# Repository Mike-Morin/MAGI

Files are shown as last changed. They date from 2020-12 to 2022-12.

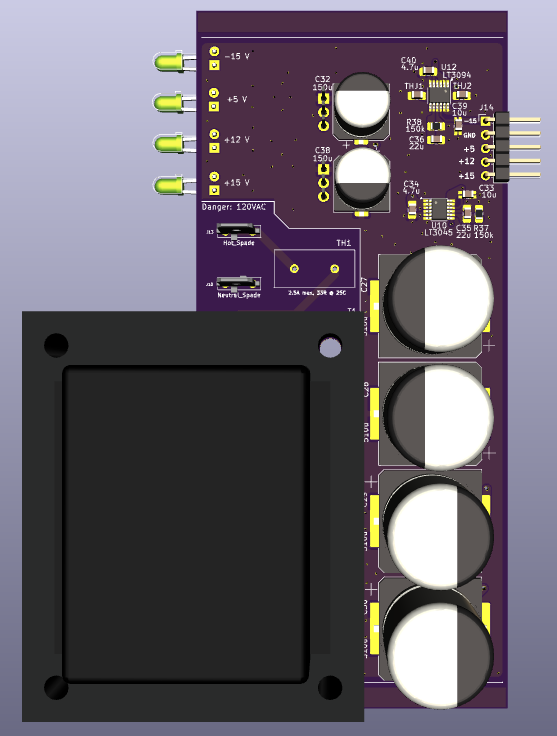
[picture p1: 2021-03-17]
SMU Test Fixture/Images/top3d.png

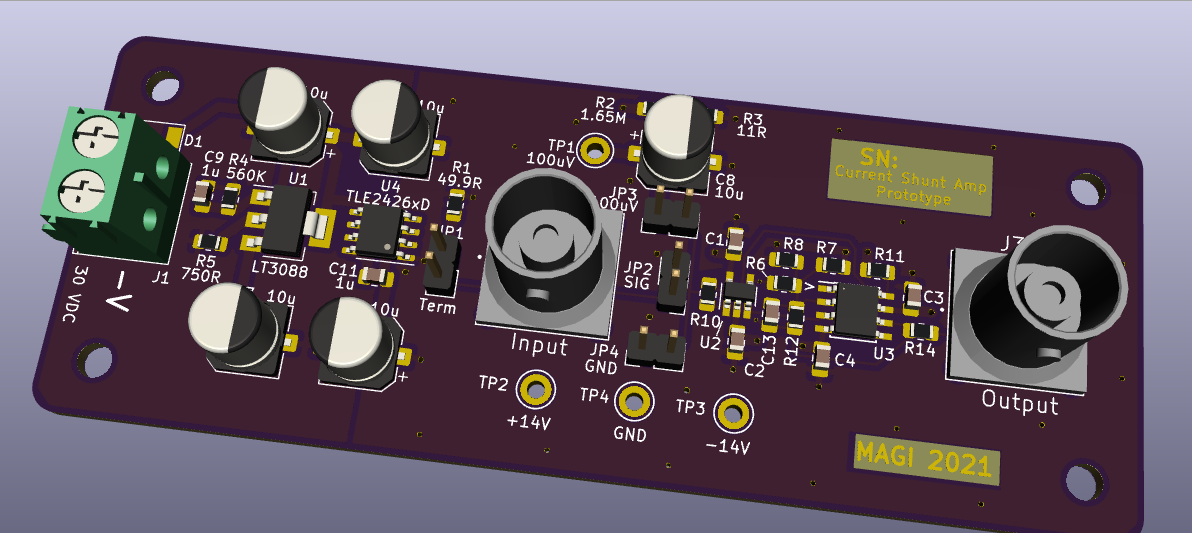
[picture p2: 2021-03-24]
SMU Shunt Amp/Images/front_3d.png

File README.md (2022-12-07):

## 363_Electrode
Electrode array with 3 input neuron contacts, 6 hidden layer contacts, and 3 output neuron contacts with dual input and output contacts for excitatory and inhibitory input and output neurons. Fits on a standard compound microscope stage and supports 12mm round coverslips for the electrode arrays.

## PetriDish
A chemotaxis game to be interfaced with a physical neural network using the Analog Discovery 2 API. Intended to train a network using reinforcement learning. An agent must follow concentration gradients to food in order to replenish energy. You can play it too.

## pnn_cs_driver
A 4 channel precision voltage controlled current source. 1mA/V, biploar 5mA+/-20nA output with 18V compliance voltage, <10ppm, 3.5 MHz bandwdith.

## SMU Test Fixture (In Progress)
16-Channel source measure unit with multiplexer for the Analog Discovery 2 (AD2). Intended to interface with a 32 pin electrode array. 

## SMU Shunt Amp (In Progress)
 - Prototype board for high speed, precision SMU Test Fixture current shunt amp.
 
## 20 Pin Electrode Connector
Pogo pin connector to bare wire. For mounting to a microscope stage and making contact with a microscope slide electrode array. This PCB goes on the stage, slides clip under the pogo pins, and a very flexible wiring harness comes off this board and into your test gear. The idea is to save a lot of money on a probe station microscope combo.

## Electrode Castellated
Microscope slide electrode array utilizing castellations as electrodes. This electrode array provides two independent cavities for testing colloidal neuromorphic devices, or, potentially, real biological neurons (use biocompatible plating such as ENIG gold). This should be epoxied to a glass slide and can be sealed over top with ports for pumping in and out materials. The cutouts allow microscopy while performing electrical excitation and measurement.

Soak FR4 boards in semiconductor grade water for a day to remove contaminant ions if precision measurements are required.

## Precision Rail Splitter
Simple precision rail splitter, currently untested. I find myself needing one of these weirdly often for experiments. The SMU Test Fixture should mostly eliminate this need.
 
## MAGI Symbols, Footprints, Models
KiCad  symbols, footprints, and models.

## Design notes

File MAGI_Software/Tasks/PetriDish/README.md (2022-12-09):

# PetriDish

A game intended to train a physical neural network, using reinforcement learning, to survive by using chemotaxis to find food in a simulated petri dish. If you want to connect a physical neural network, you'll need to install [Digilent's Waveforms](https://digilent.com/shop/software/digilent-waveforms/download) and have an appropriate device from them. PetriDish was tested with the Analog Discovery 2, but other devices from Digilent should work as long as you have DIO pins available.

## How to play
You can play using the WASD keys. Each tap increases the acceleration in that axis, but the viscosity of the petri dish will eventually slow you down.

The goal is to get food before your energy runs out. Each acceleration increase costs energy, so try to minimize your course corrections!

## How to connect a physical neural network
Using an Analog Discovery 2, you can connect up the DIO pins specified in main.py.

You'll need up, down, left, and right signals from your neural network. These allow your network to move the agent dot around in the simulated petri dish.

PetriDish will output food concentration encountered by the agent at its current location, the remaining energy available, and acceleration in separate up, down, left, and right channels as pulses
which approach max_frequency in waveforms_controller.py as those parameters approach maximum. A kill signal is also provided when the agent runs out of energy. This is to be used for training the network.

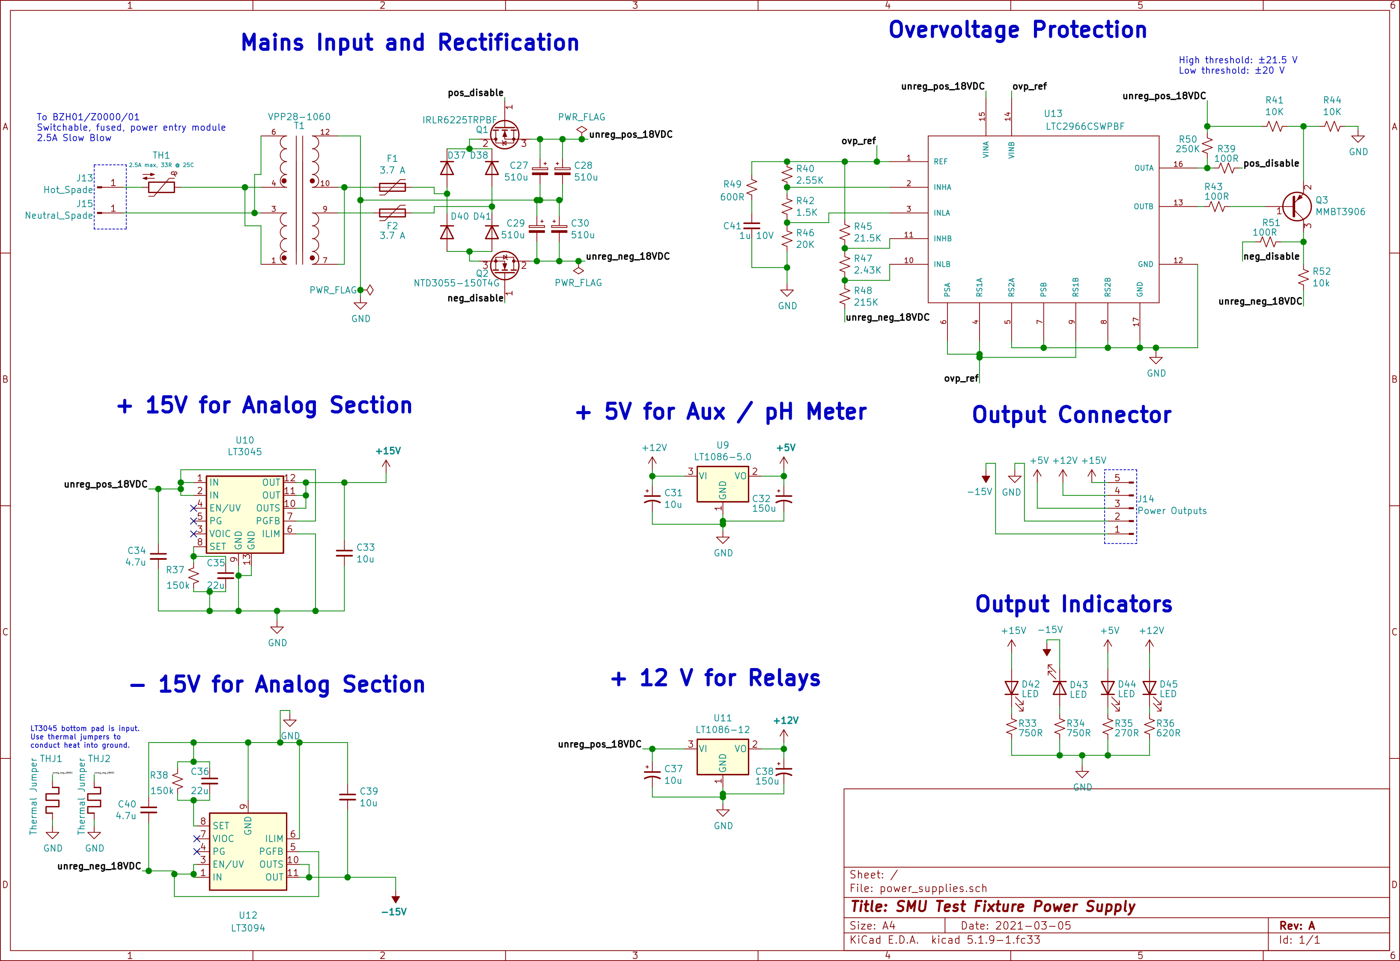
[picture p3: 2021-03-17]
SMU Test Fixture/Images/schematic.png

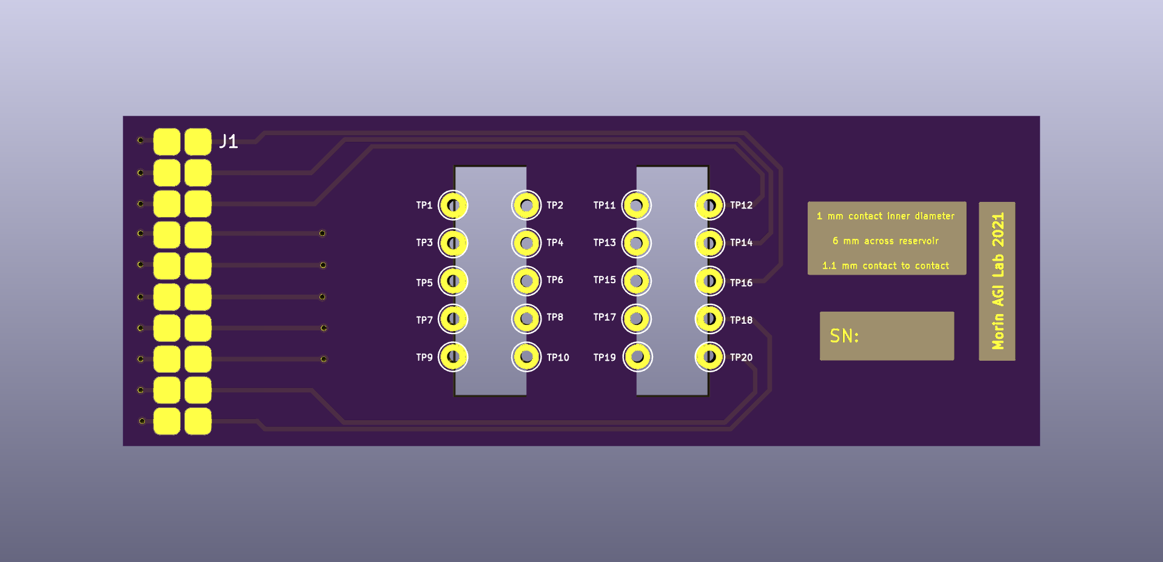
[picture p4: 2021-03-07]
Electrode_Castellated/images/Electrode_Castellated.png

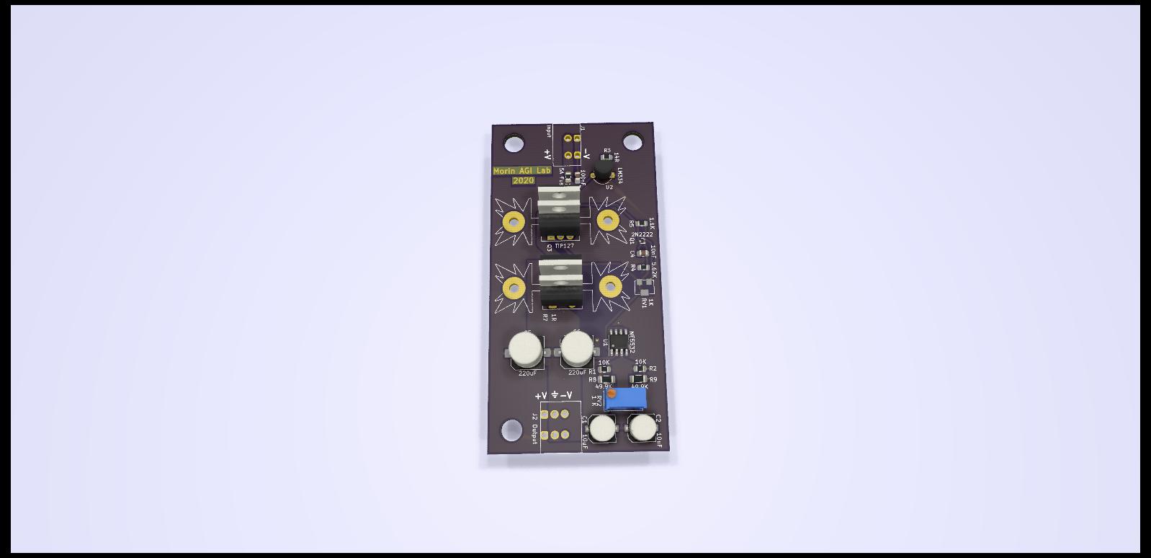
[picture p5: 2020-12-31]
Precision Rail Splitter/PNN_PS_01.jpg

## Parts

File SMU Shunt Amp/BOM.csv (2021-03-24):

Query | Qty | Manufacturer | MPN | Octopart URL | Part Description | Description | Schematic Reference | Internal Part Number | Lifecycle | Lead Time | RoHS | Total Qty (@ Batch Size: 1) | SKU | SKU | SKU | SKU | Packaging | Packaging | Packaging | Packaging | Unit Price (@ Batch Size: 1) | Unit Price (@ Batch Size: 1) | Unit Price (@ Batch Size: 1) | Unit Price (@ Batch Size: 1) | In Stock | In Stock | In Stock | In Stock | MOQ | MOQ | MOQ | MOQ | URL | URL | URL | URL | Distributor [Lowest Price (Overall)] | SKU [Lowest Price (Overall)] | Packaging [Lowest Price (Overall)] | Unit Price (@ Batch Size: 1) [Lowest Price (Overall)] | Line Total [Lowest Price (Overall)] | Batch Total [Lowest Price (Overall)] | In Stock [Lowest Price (Overall)] | MOQ [Lowest Price (Overall)] | URL [Lowest Price (Overall)] | Notes
 |  |  |  |  |  |  |  |  |  |  |  |  | Digi-Key | Future Electronics | Mouser | Newark | Digi-Key | Future Electronics | Mouser | Newark | Digi-Key | Future Electronics | Mouser | Newark | Digi-Key | Future Electronics | Mouser | Newark | Digi-Key | Future Electronics | Mouser | Newark | Digi-Key | Future Electronics | Mouser | Newark
1935161 | 1 | Phoenix Contact | 1935161 | https://octopart.com/1935161-phoenix+contact-114664 | Conn PC Terminal Block 2 POS 5mm Solder ST Thru-Hole 17.5A |  | J1 |  |  | 9w | Compliant | 1 | 277-1667-ND |  | 651-1935161 | 70R0063 | Bulk |  | Bulk |  | 0.43 |  | 0.43 | 0.536 | 0 |  | 0 | 598 | 1 |  | 1 | 1 | https://octopart.com/click/track?c=1&country=US&ct=offers&ppid=114664&sid=459&sig=08a63b4&vpid=1496254&ai4=706 |  | https://octopart.com/click/track?country=US&ct=offers&ppid=114664&sid=2401&sig=0077a68&vpid=37625215&ai4=706 | https://octopart.com/click/track?country=US&ct=offers&ppid=114664&sid=2402&sig=012689b&vpid=22101010&ai4=706 | Freelance Electronics | 1935161 |  | 0.25375 | 0.25375 | 0.25375 | 38 | 1 | https://octopart.com/click/track?country=US&ct=offers&ppid=114664&sid=13062&sig=030573c&vpid=683890266&ai4=706
TLE2426CDR | 1 | Texas Instruments | TLE2426CDR | https://octopart.com/tle2426cdr-texas+instruments-2358568 | VOLTAGE REF, VIRTUAL GRND, 2V-20V, SOIC8; MSL: MSL 1 - Unlimited; SVHC: No SVHC (15-Jan-2019) |  | U4 |  | Production (Last Updated: 3 days ago) | 6w | Compliant | 1 | 296-26774-1-ND |  | 595-TLE2426CDR | 26AJ9949 | Cut Tape |  | Tape & Reel | Cut Tape | 2.2 |  | 2.18 | 5.16 | 5577 |  | 1843 | 0 | 1 |  | 1 | 1 | https://octopart.com/click/track?country=US&ct=offers&ppid=2358568&sid=459&sig=004daac&vpid=34363295&ai4=706 |  | https://octopart.com/click/track?country=US&ct=offers&ppid=2358568&sid=2401&sig=008674c&vpid=99328580&ai4=706 | https://octopart.com/click/track?c=1&country=US&ct=offers&ppid=2358568&sid=2402&sig=010ba20&vpid=702463542&ai4=706 | Texas Instruments | TLE2426CDR | Cut Tape | 1.575 | 1.575 | 1.575 | 25205 | 1 | https://octopart.com/click/track?country=US&ct=offers&ppid=2358568&sid=27219&sig=0e3b098&vpid=510088582&ai4=706
LT3088EST#PBF | 1 | Analog Devices / Linear Technology | LT3088EST#PBF | https://octopart.com/lt3088est%23pbf-analog+devices+%2F+linear+technology-59380553 | LDO Regulator Pos 0V to 34.5V 0.8A Automotive 4-Pin(3+Tab) SOT-223 Tube |  | U1 |  | Production (Last Updated: 3 weeks ago) | 8w | Compliant | 1 | LT3088EST#PBF-ND |  | 584-LT3088EST#PBF |  | Tube |  | Tube |  | 5.2 |  | 4.91 |  | 1413 |  | 2455 |  | 1 |  | 1 |  | https://octopart.com/click/track?country=US&ct=offers&ppid=59380553&sid=459&sig=09ddf50&vpid=650441428&ai4=706 |  | https://octopart.com/click/track?country=US&ct=offers&ppid=59380553&sid=2401&sig=012dda7&vpid=457794260&ai4=706 |  | Arrow Electronics | LT3088EST#PBF |  | 4.665 | 4.665 | 4.665 | 56 | 1 | https://octopart.com/click/track?country=US&ct=offers&ppid=59380553&sid=1106&sig=0ce0df2&vpid=494966126&ai4=706
CRCW0805560KFKEA | 1 | Vishay | CRCW0805560KFKEA | https://octopart.com/crcw0805560kfkea-vishay-39855720 | Res Thick Film 0805 560K Ohm 1% 1/8W ±100ppm/°C Molded SMD SMD Paper T/R |  | R4 |  |  | 50w | Compliant | 1 | 541-560KCCT-ND | 5224258 | 71-CRCW0805-560K-E3 | 89M6822 | Cut Tape | Tape & Reel | Tape & Reel | Cut Tape | 0.1 |  | 0.1 | 0.005 | 26 | 0 | 131 | 11253 | 1 | 5000 | 1 | 1 | https://octopart.com/click/track?country=US&ct=offers&ppid=39855720&sid=459&sig=03d01a7&vpid=115678139&ai4=706 | https://octopart.com/click/track?c=1&country=US&ct=offers&ppid=39855720&sid=2454&sig=00077ac&vpid=416958915&ai4=706 | https://octopart.com/click/track?country=US&ct=offers&ppid=39855720&sid=2401&sig=070281e&vpid=115538993&ai4=706 | https://octopart.com/click/track?country=US&ct=offers&ppid=39855720&sid=2402&sig=02e692e&vpid=249262827&ai4=706 | Newark | 89M6822 | Cut Tape | 0.005 | 0.005 | 0.005 | 11253 | 1 | https://octopart.com/click/track?country=US&ct=offers&ppid=39855720&sid=2402&sig=02e692e&vpid=249262827&ai4=706
08055C105K4T4A | 1 | AVX | 08055C105K4T4A | https://octopart.com/08055c105k4t4a-avx-98101934 | Cap Ceramic 1uF 50V X7R 10% 0805T/R |  | C9 |  |  | 26w | Compliant | 1 | 478-08055C105K4T4ATR-ND |  | 581-08055C105K4T4A |  | Tape & Reel |  | Tape & Reel |  |  |  | 0.33 |  | 0 |  | 12546 |  | 10000 |  | 1 |  | https://octopart.com/click/track?c=1&country=US&ct=offers&ppid=98101934&sid=459&sig=0a200e5&vpid=597265688&ai4=706 |  | https://octopart.com/click/track?country=US&ct=offers&ppid=98101934&sid=2401&sig=066cfe1&vpid=583686534&ai4=706 |  | Mouser | 581-08055C105K4T4A | Tape & Reel | 0.33 | 0.33 | 0.33 | 12546 | 1 | https://octopart.com/click/track?country=US&ct=offers&ppid=98101934&sid=2401&sig=066cfe1&vpid=583686534&ai4=706
CRCW0805750RFKEA | 1 | Vishay | CRCW0805750RFKEA | https://octopart.com/crcw0805750rfkea-vishay-39435158 | Res Thick Film 0805 750 Ohm 1% 1/8W ±100ppm/°C Molded SMD Paper T/R |  | R5 |  |  | 52w | Compliant | 1 | 541-750CCT-ND | 9375668 | 71-CRCW0805-750-E3 | 53K0470 | Cut Tape | Cut Tape | Tape & Reel | Cut Tape | 0.1 | 0.098 | 0.1 | 0.125 | 0 | 3900 | 33045 | 6476 | 1 | 1 | 1 | 1 | https://octopart.com/click/track?c=1&country=US&ct=offers&ppid=39435158&sid=459&sig=0cefe8e&vpid=115140448&ai4=706 | https://octopart.com/click/track?country=US&ct=offers&ppid=39435158&sid=2454&sig=02609d3&vpid=416959067&ai4=706 | https://octopart.com/click/track?country=US&ct=offers&ppid=39435158&sid=2401&sig=08dcb96&vpid=114829070&ai4=706 | https://octopart.com/click/track?country=US&ct=offers&ppid=39435158&sid=2402&sig=06032ce&vpid=115417279&ai4=706 | Freelance Electronics | CRCW0805750RFKEA |  | 0.00294 | 0.00294 | 0.00294 | 4000 | 1 | https://octopart.com/click/track?country=US&ct=offers&ppid=39435158&sid=13062&sig=0cc6662&vpid=534793506&ai4=706
08055C105K4T4A | 1 | AVX | 08055C105K4T4A | https://octopart.com/08055c105k4t4a-avx-98101934 | Cap Ceramic 1uF 50V X7R 10% 0805T/R |  | C11 |  |  | 26w | Compliant | 1 | 478-08055C105K4T4ATR-ND |  | 581-08055C105K4T4A |  | Tape & Reel |  | Tape & Reel |  |  |  | 0.33 |  | 0 |  | 12546 |  | 10000 |  | 1 |  | https://octopart.com/click/track?c=1&country=US&ct=offers&ppid=98101934&sid=459&sig=0a200e5&vpid=597265688&ai4=706 |  | https://octopart.com/click/track?country=US&ct=offers&ppid=98101934&sid=2401&sig=066cfe1&vpid=583686534&ai4=706 |  | Mouser | 581-08055C105K4T4A | Tape & Reel | 0.33 | 0.33 | 0.33 | 12546 | 1 | https://octopart.com/click/track?country=US&ct=offers&ppid=98101934&sid=2401&sig=066cfe1&vpid=583686534&ai4=706
1-1337445-0 | 1 | TE Connectivity | 1-1337445-0 | https://octopart.com/1-1337445-0-te+connectivity-40794407 | Conn BNC RCP 0Hz to 4GHz 50Ohm Solder ST Thru-Hole Silver Individual |  | J2 |  | Production (Last Updated: 6 days ago) | 9w | Compliant | 1 | A101972-ND | 9135933 | 571-1-1337445-0 | 83H3471 | Box | Bag | Bulk |  | 4.08 |  | 4.04 | 4.53 | 3319 | 0 | 2178 | 1210 | 1 | 250 | 1 | 1 | https://octopart.com/click/track?country=US&ct=offers&ppid=40794407&sid=459&sig=01ce4e7&vpid=198652180&ai4=706 | https://octopart.com/click/track?c=1&country=US&ct=offers&ppid=40794407&sid=2454&sig=099450f&vpid=704876717&ai4=706 | https://octopart.com/click/track?country=US&ct=offers&ppid=40794407&sid=2401&sig=09050bd&vpid=116122491&ai4=706 | https://octopart.com/click/track?country=US&ct=offers&ppid=40794407&sid=2402&sig=04cdc58&vpid=39499681&ai4=706 | Avnet Europe | 1-1337445-0 |  | 2.16193142851737 | 2.16193142851737 | 2.16193142851737 | 2450 | 1 | https://octopart.com/click/track?country=US&ct=offers&ppid=40794407&sid=15544&sig=051fe0c&vpid=263236725&ai4=706
1-1337445-0 | 1 | TE Connectivity | 1-1337445-0 | https://octopart.com/1-1337445-0-te+connectivity-40794407 | Conn BNC RCP 0Hz to 4GHz 50Ohm Solder ST Thru-Hole Silver Individual |  | J3 |  | Production (Last Updated: 6 days ago) | 9w | Compliant | 1 | A101972-ND | 9135933 | 571-1-1337445-0 | 83H3471 | Box | Bag | Bulk |  | 4.08 |  | 4.04 | 4.53 | 3319 | 0 | 2178 | 1210 | 1 | 250 | 1 | 1 | https://octopart.com/click/track?country=US&ct=offers&ppid=40794407&sid=459&sig=01ce4e7&vpid=198652180&ai4=706 | https://octopart.com/click/track?c=1&country=US&ct=offers&ppid=40794407&sid=2454&sig=099450f&vpid=704876717&ai4=706 | https://octopart.com/click/track?country=US&ct=offers&ppid=40794407&sid=2401&sig=09050bd&vpid=116122491&ai4=706 | https://octopart.com/click/track?country=US&ct=offers&ppid=40794407&sid=2402&sig=04cdc58&vpid=39499681&ai4=706 | Avnet Europe | 1-1337445-0 |  | 2.16193142851737 | 2.16193142851737 | 2.16193142851737 | 2450 | 1 | https://octopart.com/click/track?country=US&ct=offers&ppid=40794407&sid=15544&sig=051fe0c&vpid=263236725&ai4=706
UCZ1J100MCS1GS | 1 | Nichicon | UCZ1J100MCS1GS | https://octopart.com/ucz1j100mcs1gs-nichicon-61743795 | High Reliability Low Temperature ESR specification Chip Type, 10 μ F, 63 V, -40°C to 125°C, RoHS |  | C7 |  | Production (Last Updated: 6 months ago) | 23w | Compliant | 1 | 493-UCZ1J100MCS1GSDKR-ND |  | 647-UCZ1J100MCS1GS |  | Custom Reel |  | Tape & Reel |  | 0.91 |  | 0.88 |  | 0 |  | 890 |  | 1 |  | 1 |  | https://octopart.com/click/track?c=1&country=US&ct=offers&ppid=61743795&sid=459&sig=013550e&vpid=664467063&ai4=706 |  | https://octopart.com/click/track?country=US&ct=offers&ppid=61743795&sid=2401&sig=027beab&vpid=218274266&ai4=706 |  | Mouser | 647-UCZ1J100MCS1GS | Tape & Reel | 0.88 | 0.88 | 0.88 | 890 | 1 | https://octopart.com/click/track?country=US&ct=offers&ppid=61743795&sid=2401&sig=027beab&vpid=218274266&ai4=706
PMEG4050ETP,115 | 1 | Nexperia | PMEG4050ETP,115 | https://octopart.com/pmeg4050etp%2C115-nexperia-78741518 | PMEG4050ETP - 40 V, 5 A low VF MEGA Schottky barrier rectifier |  | D1 |  | Production (Last Updated: 1 day ago) | 20w | Compliant | 1 | 1727-1732-1-ND |  | 771-PMEG4050ETP,115 | 05W5699 | Cut Tape |  | Tape & Reel |  | 0.38 |  | 0.4 |  | 3637 |  | 2692 | 3000 | 1 |  | 1 | 5 | https://octopart.com/click/track?country=US&ct=offers&ppid=78741518&sid=459&sig=01ced97&vpid=417206227&ai4=706 |  | https://octopart.com/click/track?country=US&ct=offers&ppid=78741518&sid=2401&sig=05d7ec8&vpid=416182120&ai4=706 | https://octopart.com/click/track?country=US&ct=offers&ppid=78741518&sid=2402&sig=08cc4bc&vpid=511382551&ai4=706 | Arrow Electronics | PMEG4050ETP,115 | Cut Tape | 0.3515 | 0.3515 | 0.3515 | 6077 | 1 | https://octopart.com/click/track?country=US&ct=offers&ppid=78741518&sid=1106&sig=067f840&vpid=485889811&ai4=706
C0805C103K5GEC7210 | 1 | KEMET | C0805C103K5GEC7210 | https://octopart.com/c0805c103k5gec7210-kemet-91307640 | Cap Cer 0805 10NF 50V C0G 10% |  | C4 |  |  | 16w |  | 1 | 399-C0805C103K5GEC7210CT-ND |  | 80-C0805C103K5GECLR |  | Cut Tape |  | Tape & Reel |  | 0.3 |  | 0.31 |  | 1936 |  | 4753 |  | 1 |  | 1 |  | https://octopart.com/click/track?c=1&country=US&ct=offers&ppid=91307640&sid=459&sig=0c772f1&vpid=672282118&ai4=706 |  | https://octopart.com/click/track?country=US&ct=offers&ppid=91307640&sid=2401&sig=07ac9ae&vpid=476451731&ai4=706 |  | Digi-Key | 399-C0805C103K5GEC7210CT-ND | Cut Tape | 0.3 | 0.3 | 0.3 | 1936 | 1 | https://octopart.com/click/track?c=1&country=US&ct=offers&ppid=91307640&sid=459&sig=0c772f1&vpid=672282118&ai4=706
C0805C103K5GEC7210 | 1 | KEMET | C0805C103K5GEC7210 | https://octopart.com/c0805c103k5gec7210-kemet-91307640 | Cap Cer 0805 10NF 50V C0G 10% |  | C1 |  |  | 16w |  | 1 | 399-C0805C103K5GEC7210CT-ND |  | 80-C0805C103K5GECLR |  | Cut Tape |  | Tape & Reel |  | 0.3 |  | 0.31 |  | 1936 |  | 4753 |  | 1 |  | 1 |  | https://octopart.com/click/track?c=1&country=US&ct=offers&ppid=91307640&sid=459&sig=0c772f1&vpid=672282118&ai4=706 |  | https://octopart.com/click/track?country=US&ct=offers&ppid=91307640&sid=2401&sig=07ac9ae&vpid=476451731&ai4=706 |  | Digi-Key | 399-C0805C103K5GEC7210CT-ND | Cut Tape | 0.3 | 0.3 | 0.3 | 1936 | 1 | https://octopart.com/click/track?c=1&country=US&ct=offers&ppid=91307640&sid=459&sig=0c772f1&vpid=672282118&ai4=706
C0805C103K5GEC7210 | 1 | KEMET | C0805C103K5GEC7210 | https://octopart.com/c0805c103k5gec7210-kemet-91307640 | Cap Cer 0805 10NF 50V C0G 10% |  | C2 |  |  | 16w |  | 1 | 399-C0805C103K5GEC7210CT-ND |  | 80-C0805C103K5GECLR |  | Cut Tape |  | Tape & Reel |  | 0.3 |  | 0.31 |  | 1936 |  | 4753 |  | 1 |  | 1 |  | https://octopart.com/click/track?c=1&country=US&ct=offers&ppid=91307640&sid=459&sig=0c772f1&vpid=672282118&ai4=706 |  | https://octopart.com/click/track?country=US&ct=offers&ppid=91307640&sid=2401&sig=07ac9ae&vpid=476451731&ai4=706 |  | Digi-Key | 399-C0805C103K5GEC7210CT-ND | Cut Tape | 0.3 | 0.3 | 0.3 | 1936 | 1 | https://octopart.com/click/track?c=1&country=US&ct=offers&ppid=91307640&sid=459&sig=0c772f1&vpid=672282118&ai4=706
C0805C103K5GEC7210 | 1 | KEMET | C0805C103K5GEC7210 | https://octopart.com/c0805c103k5gec7210-kemet-91307640 | Cap Cer 0805 10NF 50V C0G 10% |  | C3 |  |  | 16w |  | 1 | 399-C0805C103K5GEC7210CT-ND |  | 80-C0805C103K5GECLR |  | Cut Tape |  | Tape & Reel |  | 0.3 |  | 0.31 |  | 1936 |  | 4753 |  | 1 |  | 1 |  | https://octopart.com/click/track?c=1&country=US&ct=offers&ppid=91307640&sid=459&sig=0c772f1&vpid=672282118&ai4=706 |  | https://octopart.com/click/track?country=US&ct=offers&ppid=91307640&sid=2401&sig=07ac9ae&vpid=476451731&ai4=706 |  | Digi-Key | 399-C0805C103K5GEC7210CT-ND | Cut Tape | 0.3 | 0.3 | 0.3 | 1936 | 1 | https://octopart.com/click/track?c=1&country=US&ct=offers&ppid=91307640&sid=459&sig=0c772f1&vpid=672282118&ai4=706
OPA189IDBVR | 1 | Texas Instruments | OPA189IDBVR | https://octopart.com/opa189idbvr-texas+instruments-102282385 | Op Amp Single Zero Drift Amplifier R-R O/P ±18V/36V 5-Pin SOT-23 T/R |  | U2 |  | Production (Last Updated: 3 days ago) | 6w |  | 1 | 296-OPA189IDBVRCT-ND |  | 595-OPA189IDBVR |  | Cut Tape |  | Tape & Reel |  | 2.64 |  | 2.63 |  | 5559 |  | 7037 |  | 1 |  | 1 |  | https://octopart.com/click/track?country=US&ct=offers&ppid=102282385&sid=459&sig=0508b24&vpid=582786755&ai4=706 |  | https://octopart.com/click/track?country=US&ct=offers&ppid=102282385&sid=2401&sig=00f8ae5&vpid=565221192&ai4=706 |  | Texas Instruments | OPA189IDBVR | Cut Tape | 1.893 | 1.893 | 1.893 | 235901 | 1 | https://octopart.com/click/track?country=US&ct=offers&ppid=102282385&sid=27219&sig=080d5f9&vpid=550498582&ai4=706
RN73C2A1K47BTDF | 1 | TE Connectivity | RN73C2A1K47BTDF | https://octopart.com/rn73c2a1k47btdf-te+connectivity-42431672 | Res Thin Film 0805 1.47K Ohm 0.1% 1/10W ±10ppm/°C Molded SMD SMD Paper T/R |  | R12 |  | Production (Last Updated: 6 days ago) | 20w | Compliant | 1 | A103352CT-ND |  | 279-RN73CA-1.47K | 26M2353 | Cut Tape |  | Tape & Reel | Cut Tape | 0.94 |  | 0.74 | 0.74 | 1295 |  | 1466 | 219 | 1 |  | 1 | 1 | https://octopart.com/click/track?country=US&ct=offers&ppid=42431672&sid=459&sig=020965f&vpid=275761502&ai4=706 |  | https://octopart.com/click/track?country=US&ct=offers&ppid=42431672&sid=2401&sig=06dc8ec&vpid=247880576&ai4=706 | https://octopart.com/click/track?country=US&ct=offers&ppid=42431672&sid=2402&sig=07db9f0&vpid=254948299&ai4=706 | Arrow Electronics | RN73C2A1K47BTDF | Cut Tape | 0.2121 | 0.2121 | 0.2121 | 650 | 1 | https://octopart.com/click/track?country=US&ct=offers&ppid=42431672&sid=1106&sig=027ba51&vpid=473458999&ai4=706
CPF0805B15RE1 | 1 | TE Connectivity | CPF0805B15RE1 | https://octopart.com/cpf0805b15re1-te+connectivity-9539446 | Res Thin Film 0805 15 Ohm 0.1% 1/10W ±25ppm/°C Molded SMD SMD Paper T/R |  | R8 |  | Production (Last Updated: 6 days ago) | 21w | Compliant | 1 | A103157CT-ND | 1117806 | 279-CPF0805B15RE1 | 80P3962 | Cut Tape | Tape & Reel | Tape & Reel | Cut Tape | 0.59 |  | 0.58 | 0.036 | 1168 | 1000 | 1337 | 4 | 1 | 1000 | 1 | 1 | https://octopart.com/click/track?country=US&ct=offers&ppid=9539446&sid=459&sig=03bdd68&vpid=275700798&ai4=706 | https://octopart.com/click/track?c=1&country=US&ct=offers&ppid=9539446&sid=2454&sig=02ec34b&vpid=657156454&ai4=706 | https://octopart.com/click/track?country=US&ct=offers&ppid=9539446&sid=2401&sig=05fe21d&vpid=81543979&ai4=706 | https://octopart.com/click/track?country=US&ct=offers&ppid=9539446&sid=2402&sig=0ff3d52&vpid=324565392&ai4=706 | Newark | 80P3962 | Cut Tape | 0.036 | 0.036 | 0.036 | 4 | 1 | https://octopart.com/click/track?country=US&ct=offers&ppid=9539446&sid=2402&sig=0ff3d52&vpid=324565392&ai4=706
RN73C2A1K47BTDF | 1 | TE Connectivity | RN73C2A1K47BTDF | https://octopart.com/rn73c2a1k47btdf-te+connectivity-42431672 | Res Thin Film 0805 1.47K Ohm 0.1% 1/10W ±10ppm/°C Molded SMD SMD Paper T/R |  | R7 |  | Production (Last Updated: 6 days ago) | 20w | Compliant | 1 | A103352CT-ND |  | 279-RN73CA-1.47K | 26M2353 | Cut Tape |  | Tape & Reel | Cut Tape | 0.94 |  | 0.74 | 0.74 | 1295 |  | 1466 | 219 | 1 |  | 1 | 1 | https://octopart.com/click/track?country=US&ct=offers&ppid=42431672&sid=459&sig=020965f&vpid=275761502&ai4=706 |  | https://octopart.com/click/track?country=US&ct=offers&ppid=42431672&sid=2401&sig=06dc8ec&vpid=247880576&ai4=706 | https://octopart.com/click/track?country=US&ct=offers&ppid=42431672&sid=2402&sig=07db9f0&vpid=254948299&ai4=706 | Arrow Electronics | RN73C2A1K47BTDF | Cut Tape | 0.2121 | 0.2121 | 0.2121 | 650 | 1 | https://octopart.com/click/track?country=US&ct=offers&ppid=42431672&sid=1106&sig=027ba51&vpid=473458999&ai4=706
CRCW08051M00FKEA | 1 | Vishay | CRCW08051M00FKEA | https://octopart.com/crcw08051m00fkea-vishay-40019056 | Res Thick Film 0805 1M Ohm 1% 0.125W(1/8W) +/-100ppm/ßC Pad SMD Automotive T/R |  | R10 |  |  | 52w | Compliant | 1 | 541-1.00MCCT-ND | 3244027 | 71-CRCW0805-1.0M-E3 | 25AC7639 | Cut Tape | Cut Tape | Tape & Reel |  | 0.1 | 0.098 | 0.1 |  | 36164 | 4806 | 303 | 0 | 1 | 1 | 1 | 5000 | https://octopart.com/click/track?country=US&ct=offers&ppid=40019056&sid=459&sig=0217c53&vpid=114978865&ai4=706 | https://octopart.com/click/track?country=US&ct=offers&ppid=40019056&sid=2454&sig=08233a8&vpid=416958368&ai4=706 | https://octopart.com/click/track?country=US&ct=offers&ppid=40019056&sid=2401&sig=03d8181&vpid=114828969&ai4=706 | https://octopart.com/click/track?country=US&ct=offers&ppid=40019056&sid=2402&sig=05beceb&vpid=508832299&ai4=706 | Freelance Electronics | CRCW08051M00FKEA |  | 0.00274 | 0.00274 | 0.00274 | 4760 | 1 | https://octopart.com/click/track?country=US&ct=offers&ppid=40019056&sid=13062&sig=06062b2&vpid=165656522&ai4=706
CRCW080520K0FKEAC | 1 | Vishay | CRCW080520K0FKEAC | https://octopart.com/crcw080520k0fkeac-vishay-22248124 | Res Thick Film 0805 20K Ohm 1% 1/8W ±100ppm/°C Molded SMD Paper T/R |  | R11 |  |  | 22w | Compliant | 1 | 541-4133-1-ND | 9114504 | 71-CRCW080520K0FKEAC | 98AC1033 | Cut Tape | Cut Tape | Tape & Reel |  | 0.1 | 0.098 | 0.1 |  | 159674 | 113550 | 52194 | 0 | 1 | 1 | 1 | 5000 | https://octopart.com/click/track?country=US&ct=offers&ppid=22248124&sid=459&sig=0031e19&vpid=454353781&ai4=706 | https://octopart.com/click/track?country=US&ct=offers&ppid=22248124&sid=2454&sig=0038973&vpid=657069195&ai4=706 | https://octopart.com/click/track?country=US&ct=offers&ppid=22248124&sid=2401&sig=06ca467&vpid=458954182&ai4=706 | https://octopart.com/click/track?country=US&ct=offers&ppid=22248124&sid=2402&sig=07fd920&vpid=634341003&ai4=706 | Future Electronics | 9114504 | Cut Tape | 0.098 | 0.098 | 0.098 | 113550 | 1 | https://octopart.com/click/track?country=US&ct=offers&ppid=22248124&sid=2454&sig=0038973&vpid=657069195&ai4=706
CRCW080549R9FKEA | 1 | Vishay | CRCW080549R9FKEA | https://octopart.com/crcw080549r9fkea-vishay-39436139 | Res Thick Film 0805 49.9 Ohm 1% 1/8W ±100ppm/°C Molded SMD Paper T/R |  | R14 |  |  | 52w | Compliant | 1 | 541-49.9CCT-ND | 1522234 | 71-CRCW0805-49.9-E3 | 61M5502 | Cut Tape | Cut Tape | Tape & Reel | Cut Tape | 0.1 | 0.098 | 0.1 | 0.125 | 0 | 3577 | 33208 | 1055 | 1 | 1 | 1 | 1 | https://octopart.com/click/track?c=1&country=US&ct=offers&ppid=39436139&sid=459&sig=02e283f&vpid=114978997&ai4=706 | https://octopart.com/click/track?country=US&ct=offers&ppid=39436139&sid=2454&sig=0c3ced1&vpid=416958842&ai4=706 | https://octopart.com/click/track?country=US&ct=offers&ppid=39436139&sid=2401&sig=0eefc03&vpid=114829038&ai4=706 | https://octopart.com/click/track?country=US&ct=offers&ppid=39436139&sid=2402&sig=0afc929&vpid=115417053&ai4=706 | Freelance Electronics | CRCW080549R9FKEA |  | 0.00294 | 0.00294 | 0.00294 | 4000 | 1 | https://octopart.com/click/track?country=US&ct=offers&ppid=39436139&sid=13062&sig=0afb55d&vpid=619428780&ai4=706
RQ73C2A11RBTDF | 1 | TE Connectivity / Holsworthy | RQ73C2A11RBTDF | https://octopart.com/rq73c2a11rbtdf-te+connectivity+%2F+holsworthy-100695032 | Res Precision Thin Film 0805 11 Ohm 0.1% 1/5W ±10ppm/°C Molded T/R |  | R3 |  | Production (Last Updated: 6 days ago) | 15w | Compliant | 1 |  |  | 279-RQ73C2A11RBTDF | 97AC0236 |  |  | Tape & Reel | Cut Tape |  |  | 0.78 | 0.331 |  |  | 968 | 1000 |  |  | 1 | 1 |  |  | https://octopart.com/click/track?country=US&ct=offers&ppid=100695032&sid=2401&sig=0bb45c2&vpid=530989355&ai4=706 | https://octopart.com/click/track?country=US&ct=offers&ppid=100695032&sid=2402&sig=069a865&vpid=537806156&ai4=706 | Newark | 97AC0236 | Cut Tape | 0.331 | 0.331 | 0.331 | 1000 | 1 | https://octopart.com/click/track?country=US&ct=offers&ppid=100695032&sid=2402&sig=069a865&vpid=537806156&ai4=706
RC0805FR-071M65L | 1 | Yageo | RC0805FR-071M65L | https://octopart.com/rc0805fr-071m65l-yageo-1453716 | Res Thick Film 0805 1.65M Ohm 1% 1/8W ±100ppm/°C Molded SMD SMD Paper T/R |  | R2 |  |  | 20w | Compliant | 1 | 311-1.65MCRCT-ND | 7081413 | 603-RC0805FR-071M65L |  | Cut Tape | Tape & Reel | Tape & Reel |  | 0.1 |  | 0.13 |  | 2757 | 5000 | 11776 |  | 1 | 5000 | 1 |  | https://octopart.com/click/track?country=US&ct=offers&ppid=1453716&sid=459&sig=0a7fb45&vpid=1991217&ai4=706 | https://octopart.com/click/track?country=US&ct=offers&ppid=1453716&sid=2454&sig=0b85164&vpid=454336852&ai4=706 | https://octopart.com/click/track?country=US&ct=offers&ppid=1453716&sid=2401&sig=0152698&vpid=210304720&ai4=706 |  | Quest | RC0805FR-071M65L |  | 0.0112 | 0.0112 | 0.0112 | 3545 | 1 | https://octopart.com/click/track?country=US&ct=offers&ppid=1453716&sid=2412&sig=02857ae&vpid=261389810&ai4=706
CRCW080549R9FKEA | 1 | Vishay | CRCW080549R9FKEA | https://octopart.com/crcw080549r9fkea-vishay-39436139 | Res Thick Film 0805 49.9 Ohm 1% 1/8W ±100ppm/°C Molded SMD Paper T/R |  | R1 |  |  | 52w | Compliant | 1 | 541-49.9CCT-ND | 1522234 | 71-CRCW0805-49.9-E3 | 61M5502 | Cut Tape | Cut Tape | Tape & Reel | Cut Tape | 0.1 | 0.098 | 0.1 | 0.125 | 0 | 3577 | 33208 | 1055 | 1 | 1 | 1 | 1 | https://octopart.com/click/track?c=1&country=US&ct=offers&ppid=39436139&sid=459&sig=02e283f&vpid=114978997&ai4=706 | https://octopart.com/click/track?country=US&ct=offers&ppid=39436139&sid=2454&sig=0c3ced1&vpid=416958842&ai4=706 | https://octopart.com/click/track?country=US&ct=offers&ppid=39436139&sid=2401&sig=0eefc03&vpid=114829038&ai4=706 | https://octopart.com/click/track?country=US&ct=offers&ppid=39436139&sid=2402&sig=0afc929&vpid=115417053&ai4=706 | Freelance Electronics | CRCW080549R9FKEA |  | 0.00294 | 0.00294 | 0.00294 | 4000 | 1 | https://octopart.com/click/track?country=US&ct=offers&ppid=39436139&sid=13062&sig=0afb55d&vpid=619428780&ai4=706
5011 | 1 | Keystone | 5011 | https://octopart.com/5011-keystone-8542 | Test Point MultiPurpose THM H .445 Nylon 46 Insulated Blk PhosBronze/Silver |  | TP1 |  |  | 6w | Compliant | 1 | 36-5011-ND | 5322706 | 534-5011 | 88H2535 | Bulk | Box | Bulk |  | 0.42 | 0.158 | 0.35 | 0.354 | 265046 | 80684 | 54358 | 33643 | 1 | 1 | 1 | 1 | https://octopart.com/click/track?country=US&ct=offers&ppid=8542&sid=459&sig=0f2083a&vpid=212427649&ai4=706 | https://octopart.com/click/track?country=US&ct=offers&ppid=8542&sid=2454&sig=0b37936&vpid=19657341&ai4=706 | https://octopart.com/click/track?country=US&ct=offers&ppid=8542&sid=2401&sig=03ac86d&vpid=37625720&ai4=706 | https://octopart.com/click/track?country=US&ct=offers&ppid=8542&sid=2402&sig=0e990a9&vpid=78611211&ai4=706 | Voyager Components | 5011-KEYSTONE-N/A |  | 0.144 | 0.144 | 0.144 | 111 | 1 | https://octopart.com/click/track?country=US&ct=offers&ppid=8542&sid=2424&sig=0178ff4&vpid=705009728&ai4=706
22-28-5027 | 1 | Molex | 22-28-5027 | https://octopart.com/22-28-5027-molex-7675655 | Header Connector, pcb Mount, recept, 2 Contacts, pin, 0.1 Pitch, pc Tail W/retnn Terminal |  | JP2 |  | Production (Last Updated: 7 months ago) | 13w | Compliant | 1 | WM21023-ND |  | 538-22-28-5027 | 56H2256 | Bulk |  | Bulk |  | 0.19 |  | 0.19 |  | 31896 |  | 29666 | 0 | 1 |  | 1 | 30000 | https://octopart.com/click/track?country=US&ct=offers&ppid=7675655&sid=459&sig=0d90284&vpid=477230934&ai4=706 |  | https://octopart.com/click/track?country=US&ct=offers&ppid=7675655&sid=2401&sig=0fc0854&vpid=84452797&ai4=706 | https://octopart.com/click/track?c=1&country=US&ct=offers&ppid=7675655&sid=2402&sig=009d51f&vpid=578966298&ai4=706 | Arrow Electronics | 22-28-5027 |  | 0.0567 | 0.0567 | 0.0567 | 0 | 1 | https://octopart.com/click/track?c=1&country=US&ct=offers&ppid=7675655&sid=1106&sig=0e7019f&vpid=473315866&ai4=706
22-28-5027 | 1 | Molex | 22-28-5027 | https://octopart.com/22-28-5027-molex-7675655 | Header Connector, pcb Mount, recept, 2 Contacts, pin, 0.1 Pitch, pc Tail W/retnn Terminal |  | JP3 |  | Production (Last Updated: 7 months ago) | 13w | Compliant | 1 | WM21023-ND |  | 538-22-28-5027 | 56H2256 | Bulk |  | Bulk |  | 0.19 |  | 0.19 |  | 31896 |  | 29666 | 0 | 1 |  | 1 | 30000 | https://octopart.com/click/track?country=US&ct=offers&ppid=7675655&sid=459&sig=0d90284&vpid=477230934&ai4=706 |  | https://octopart.com/click/track?country=US&ct=offers&ppid=7675655&sid=2401&sig=0fc0854&vpid=84452797&ai4=706 | https://octopart.com/click/track?c=1&country=US&ct=offers&ppid=7675655&sid=2402&sig=009d51f&vpid=578966298&ai4=706 | Arrow Electronics | 22-28-5027 |  | 0.0567 | 0.0567 | 0.0567 | 0 | 1 | https://octopart.com/click/track?c=1&country=US&ct=offers&ppid=7675655&sid=1106&sig=0e7019f&vpid=473315866&ai4=706
22-28-5027 | 1 | Molex | 22-28-5027 | https://octopart.com/22-28-5027-molex-7675655 | Header Connector, pcb Mount, recept, 2 Contacts, pin, 0.1 Pitch, pc Tail W/retnn Terminal |  | JP4 |  | Production (Last Updated: 7 months ago) | 13w | Compliant | 1 | WM21023-ND |  | 538-22-28-5027 | 56H2256 | Bulk |  | Bulk |  | 0.19 |  | 0.19 |  | 31896 |  | 29666 | 0 | 1 |  | 1 | 30000 | https://octopart.com/click/track?country=US&ct=offers&ppid=7675655&sid=459&sig=0d90284&vpid=477230934&ai4=706 |  | https://octopart.com/click/track?country=US&ct=offers&ppid=7675655&sid=2401&sig=0fc0854&vpid=84452797&ai4=706 | https://octopart.com/click/track?c=1&country=US&ct=offers&ppid=7675655&sid=2402&sig=009d51f&vpid=578966298&ai4=706 | Arrow Electronics | 22-28-5027 |  | 0.0567 | 0.0567 | 0.0567 | 0 | 1 | https://octopart.com/click/track?c=1&country=US&ct=offers&ppid=7675655&sid=1106&sig=0e7019f&vpid=473315866&ai4=706
22-28-5027 | 1 | Molex | 22-28-5027 | https://octopart.com/22-28-5027-molex-7675655 | Header Connector, pcb Mount, recept, 2 Contacts, pin, 0.1 Pitch, pc Tail W/retnn Terminal |  | JP1 |  | Production (Last Updated: 7 months ago) | 13w | Compliant | 1 | WM21023-ND |  | 538-22-28-5027 | 56H2256 | Bulk |  | Bulk |  | 0.19 |  | 0.19 |  | 31896 |  | 29666 | 0 | 1 |  | 1 | 30000 | https://octopart.com/click/track?country=US&ct=offers&ppid=7675655&sid=459&sig=0d90284&vpid=477230934&ai4=706 |  | https://octopart.com/click/track?country=US&ct=offers&ppid=7675655&sid=2401&sig=0fc0854&vpid=84452797&ai4=706 | https://octopart.com/click/track?c=1&country=US&ct=offers&ppid=7675655&sid=2402&sig=009d51f&vpid=578966298&ai4=706 | Arrow Electronics | 22-28-5027 |  | 0.0567 | 0.0567 | 0.0567 | 0 | 1 | https://octopart.com/click/track?c=1&country=US&ct=offers&ppid=7675655&sid=1106&sig=0e7019f&vpid=473315866&ai4=706
CRCW08050000Z0EB | 1 | Vishay | CRCW08050000Z0EB | https://octopart.com/crcw08050000z0eb-vishay-42466300 | Res Thick Film 0805 0 Ohm Jumper Molded SMD Paper T/R |  | R6 |  |  | 50w | Compliant | 1 | 541-CRCW08050000Z0EBCT-ND | 7457609 | 71-CRCW08050000Z0EB | 48P9971 | Cut Tape | Tape & Reel | Tape & Reel | Cut Tape | 0.1 |  | 0.1 | 0.125 | 0 | 0 | 41351 | 2978 | 1 | 10000 | 1 | 1 | https://octopart.com/click/track?c=1&country=US&ct=offers&ppid=42466300&sid=459&sig=0c44cd2&vpid=600488165&ai4=706 | https://octopart.com/click/track?c=1&country=US&ct=offers&ppid=42466300&sid=2454&sig=05e0ce0&vpid=416958114&ai4=706 | https://octopart.com/click/track?country=US&ct=offers&ppid=42466300&sid=2401&sig=08af8ca&vpid=115538939&ai4=706 | https://octopart.com/click/track?country=US&ct=offers&ppid=42466300&sid=2402&sig=0879598&vpid=115416300&ai4=706 | Mouser | 71-CRCW08050000Z0EB | Tape & Reel | 0.1 | 0.1 | 0.1 | 41351 | 1 | https://octopart.com/click/track?country=US&ct=offers&ppid=42466300&sid=2401&sig=08af8ca&vpid=115538939&ai4=706
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

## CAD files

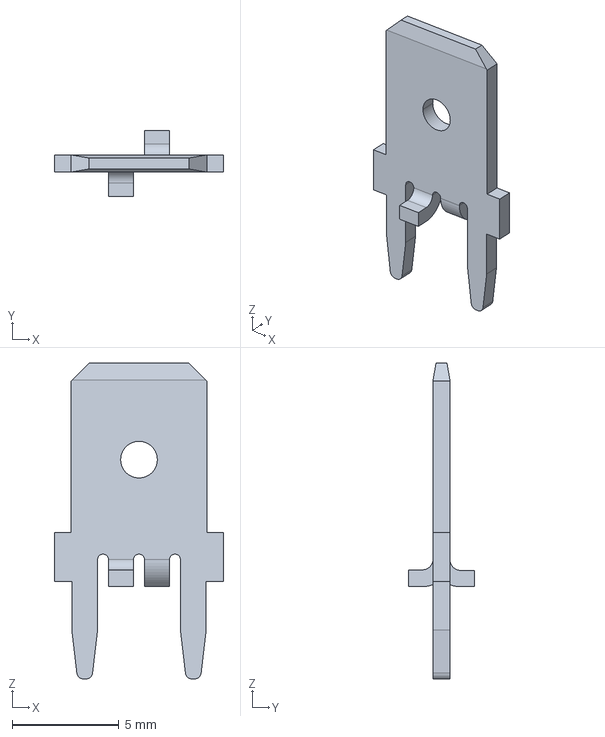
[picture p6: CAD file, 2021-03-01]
MAGI_Models/1217136-1--3DModel-STEP-1.STEP
7.92 x 3.07 x 14.8 mm

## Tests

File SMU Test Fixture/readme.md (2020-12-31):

## Source Measure Unit Test Fixture

- Characterize nanocolloidal and solid state neuromorphic devices.
  - Measure impedance changes as a result of precise excitation charges and flux-linkages over a large and precise range of excitation input values.
  - Picocoulomb and picovolt-seconds targeted.
  
- Relay multiplexer to interface with up to 16 devices.

- Utilizes Analog Discovery 2 (AD2) for analog measurement and relay control.
  - Aux power and scope input (for pH meter in this project).
  - Provides isolated, clean power for AD2.
  - Exposes AD2 ports for pass-through (AD2 is still useful for other projects).
  - Selectable fully differential and single ended scope modes.
  - "Automatic" AD2 calibration with external multimeter.
  - Internal impedance analyzer shunt resistor selector.
  
 - External excitation and multimeter inputs.

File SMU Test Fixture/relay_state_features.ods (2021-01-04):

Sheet: Features
Relay | AD2 Calibrate, Measure WG1 | AD2 Calibrate, Measure WG2 | AD2 Calibrate, Zero Scopes | AD2 Calibrate, Scopes to WG1 | Current Excitation | Voltage Excitation
ext_src_sel-s |  |  |  |  | 1 | 1
impa_sel_a |  |  |  |  | 1 | 1
impa_sel_b |  |  |  |  | 1 | 1
impa_sel_c
3x_gain_en |  |  |  |  | 0 | 1
shunt_sel |  |  |  |  | computed
sense_sel |  |  |  |  | computed
cur_volt_mod_sel |  |  |  |  | 1 | 0
shunt_sens_sel |  |  |  |  | computed
int_rst |  |  |  |  | 1 → 0 toggle | 1 → 0 toggle
ext_50_ohm
ext_meas_sel_b | 1 | 0 |  | 0
ext_meas_sel_a | 1 | 1 | 0 | 1
ext_single_diff |  |  | 1 | 1
ext_acdc_n |  |  | 1 | 1
ext_acdc_p |  | 0 | 1 | 0
scope1_mux_a
scope1_mux_b |  |  | 0 | 0
scope1_mux_c |  |  | 1 | 1
scope2_mux |  |  | 1 | 1
dut_sel_1
dut_sel_2
dut_sel_3
dut_sel_4
dut_sel_5
dut_sel_6
dut_sel_7
dut_sel_8
dut_sel_9
dut_sel_10
dut_sel_11
dut_sel_12
dut_sel_13
dut_sel_14
dut_sel_15
dut_sel_16
Set (1), Reset (0), Don’t Care ( ,x)

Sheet: Relay Locations
Designation | Relay | Top level | Imp analyzer | Ammeter and Charge Integrator | I/O and Panel | Scope meas Sel | Dut selector | All
K1 | ext_src_sel-s | 1 |  |  |  |  |  | 1
K2 | impa_sel_a |  | 1 |  |  |  |  | 1
K3 | impa_sel_b |  | 1 |  |  |  |  | 1
K4 | impa_sel_c |  | 1 |  |  |  |  | 1
K5 | 3x_gain_en |  |  | 1 |  |  |  | 1
K6 | shunt_sel |  |  | 1 |  |  |  | 1
K7 | sense_sel |  |  | 1 |  |  |  | 1
K8 | cur_volt_mod_sel |  |  | 1 |  |  |  | 1
K9 | shunt_sens_sel |  |  | 1 |  |  |  | 1
K10 | int_rst |  |  | 1 |  |  |  | 1
K11 | ext_50_ohm |  |  |  | 1 |  |  | 1
K12 | ext_meas_sel_b |  |  |  | 1 |  |  | 1
K13 | ext_meas_sel_a |  |  |  | 1 |  |  | 1
K14 | ext_single_diff |  |  |  | 1 |  |  | 1
K15 | ext_acdc_n |  |  |  | 1 |  |  | 1
K16 | ext_acdc_p |  |  |  | 1 |  |  | 1
K17 | scope1_mux_a |  |  |  |  | 1 |  | 1
K18 | scope1_mux_b |  |  |  |  | 1 |  | 1
K19 | scope1_mux_c |  |  |  |  | 1 |  | 1
K20 | scope2_mux |  |  |  |  | 1 |  | 1
K21 | dut_sel_1 |  |  |  |  |  | 1 | 1
K22 | dut_sel_2 |  |  |  |  |  | 1 | 1
K23 | dut_sel_3 |  |  |  |  |  | 1 | 1
K24 | dut_sel_4 |  |  |  |  |  | 1 | 1
K25 | dut_sel_5 |  |  |  |  |  | 1 | 1
K26 | dut_sel_6 |  |  |  |  |  | 1 | 1
K27 | dut_sel_7 |  |  |  |  |  | 1 | 1
K28 | dut_sel_8 |  |  |  |  |  | 1 | 1
K29 | dut_sel_9 |  |  |  |  |  | 1 | 1
K30 | dut_sel_10 |  |  |  |  |  | 1 | 1
K31 | dut_sel_11 |  |  |  |  |  | 1 | 1
K32 | dut_sel_12 |  |  |  |  |  | 1 | 1
K33 | dut_sel_13 |  |  |  |  |  | 1 | 1
K34 | dut_sel_14 |  |  |  |  |  | 1 | 1
K35 | dut_sel_15 |  |  |  |  |  | 1 | 1
K36 | dut_sel_16 |  |  |  |  |  | 1 | 1
 | Total | 1 | 3 | 6 | 6 | 4 | 16 | 36

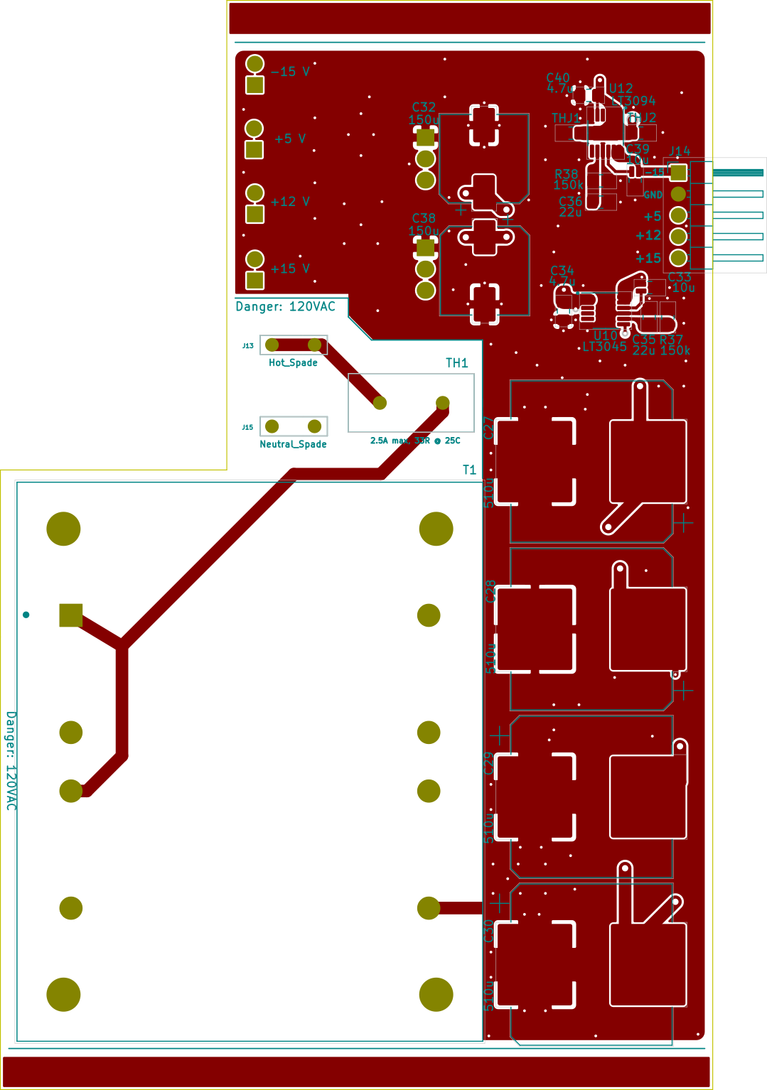
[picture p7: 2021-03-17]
SMU Test Fixture/Images/top2d.png

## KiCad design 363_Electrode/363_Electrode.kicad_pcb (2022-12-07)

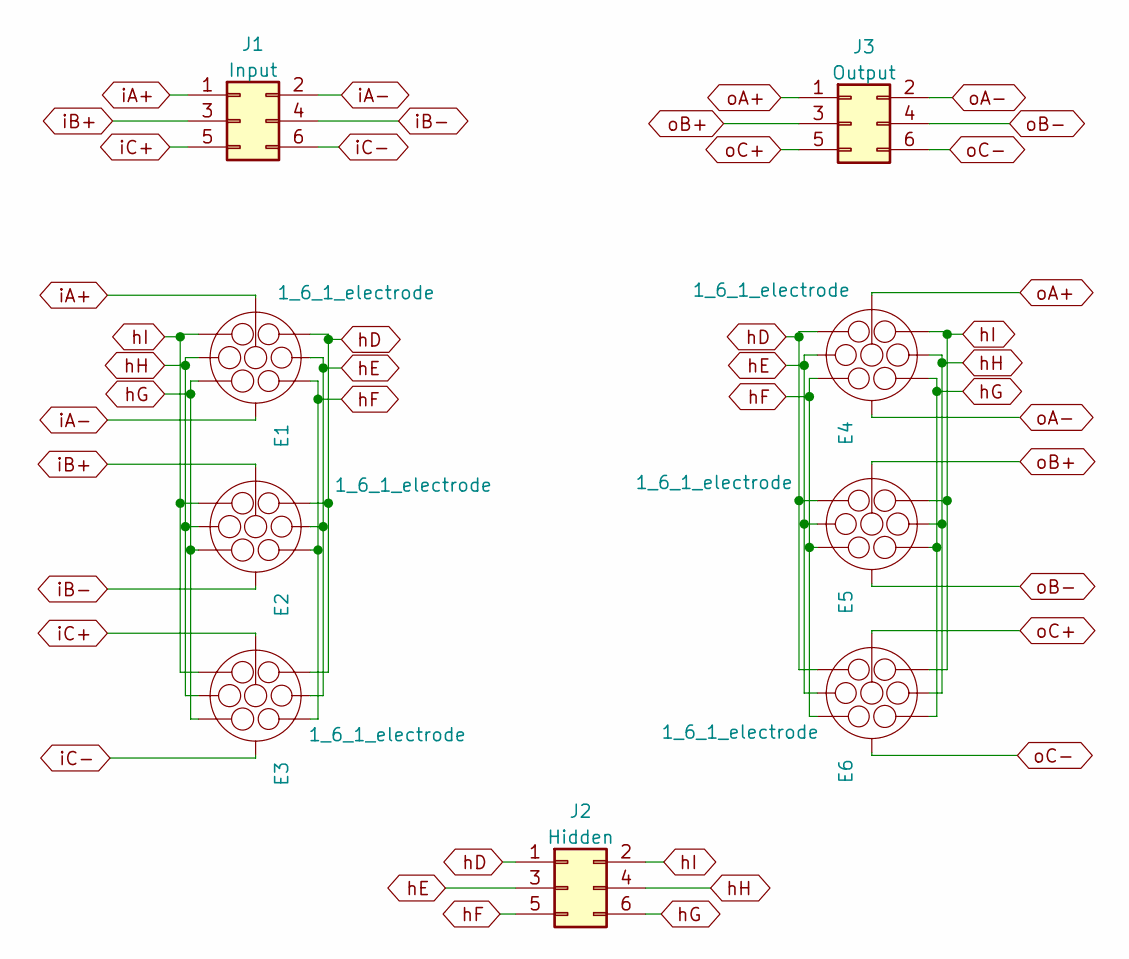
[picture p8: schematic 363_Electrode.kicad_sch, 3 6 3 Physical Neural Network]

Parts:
E1, E2, E3, E4, E5, E6: 1_6_1_electrode
J1: Input; PinHeader_2x03_P2.54mm_Vertical_SMD
J2: Hidden; PinHeader_2x03_P2.54mm_Vertical_SMD
J3: Output; PinHeader_2x03_P2.54mm_Vertical_SMD

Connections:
hD: E1.7 (H6), E2.7 (H6), E3.7 (H6), E4.7 (H6), E5.7 (H6), E6.7 (H6), J2.1
hE: E1.2 (H1), E2.2 (H1), E3.2 (H1), E4.2 (H1), E5.2 (H1), E6.2 (H1), J2.3
hF: E1.3 (H2), E2.3 (H2), E3.3 (H2), E4.3 (H2), E5.3 (H2), E6.3 (H2), J2.5
hG: E1.4 (H3), E2.4 (H3), E3.4 (H3), E4.4 (H3), E5.4 (H3), E6.4 (H3), J2.6
hH: E1.5 (H4), E2.5 (H4), E3.5 (H4), E4.5 (H4), E5.5 (H4), E6.5 (H4), J2.4
hI: E1.6 (H5), E2.6 (H5), E3.6 (H5), E4.6 (H5), E5.6 (H5), E6.6 (H5), J2.2
iA+: E1.1 (C), J1.1
iA-: E1.8 (R), J1.2
iB+: E2.1 (C), J1.3
iB-: E2.8 (R), J1.4
iC+: E3.1 (C), J1.5
iC-: E3.8 (R), J1.6
oA+: E4.1 (C), J3.1
oA-: E4.8 (R), J3.2
oB+: E5.1 (C), J3.3
oB-: E5.8 (R), J3.4
oC+: E6.1 (C), J3.5
oC-: E6.8 (R), J3.6

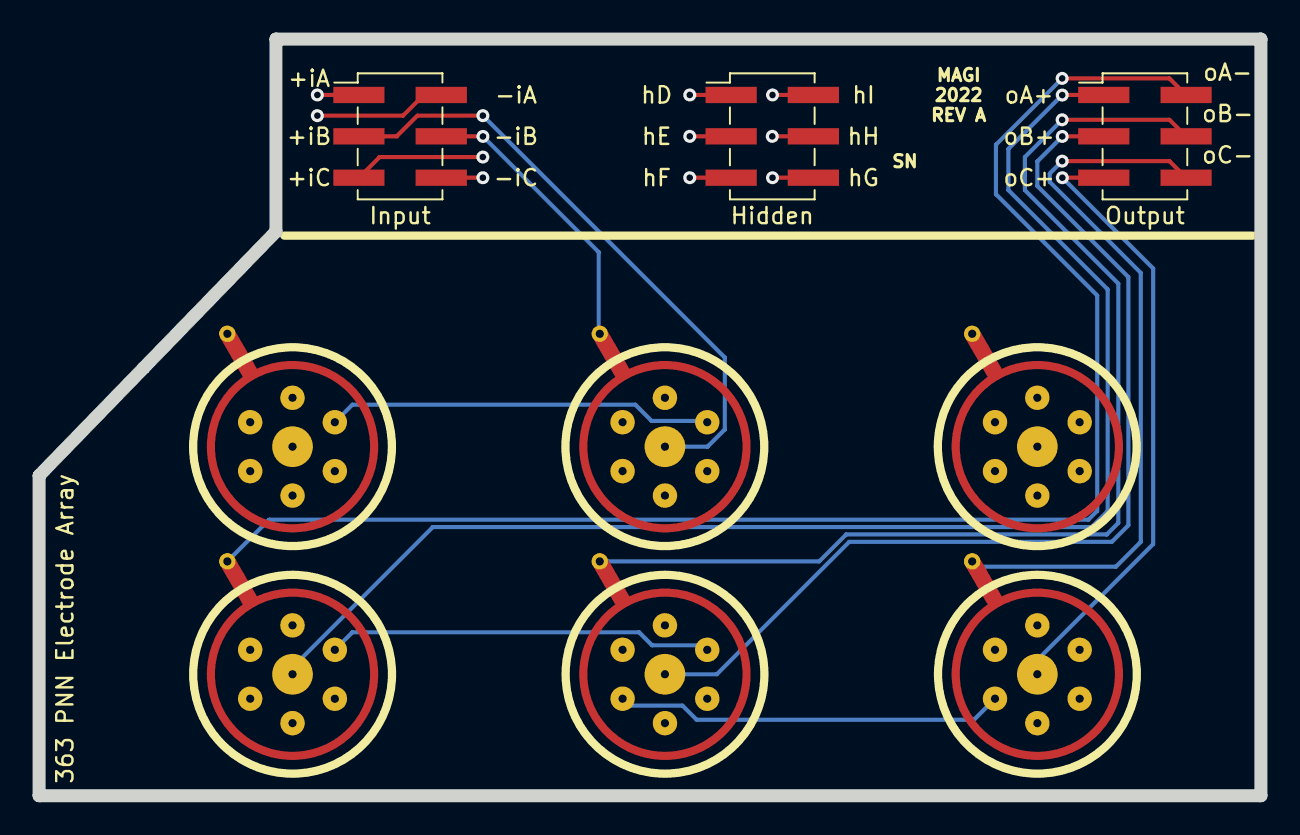
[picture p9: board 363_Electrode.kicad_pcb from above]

Board: 4 copper layers, 75.0 x 46.4 mm, 9 parts (0 on the bottom side), 18 nets.

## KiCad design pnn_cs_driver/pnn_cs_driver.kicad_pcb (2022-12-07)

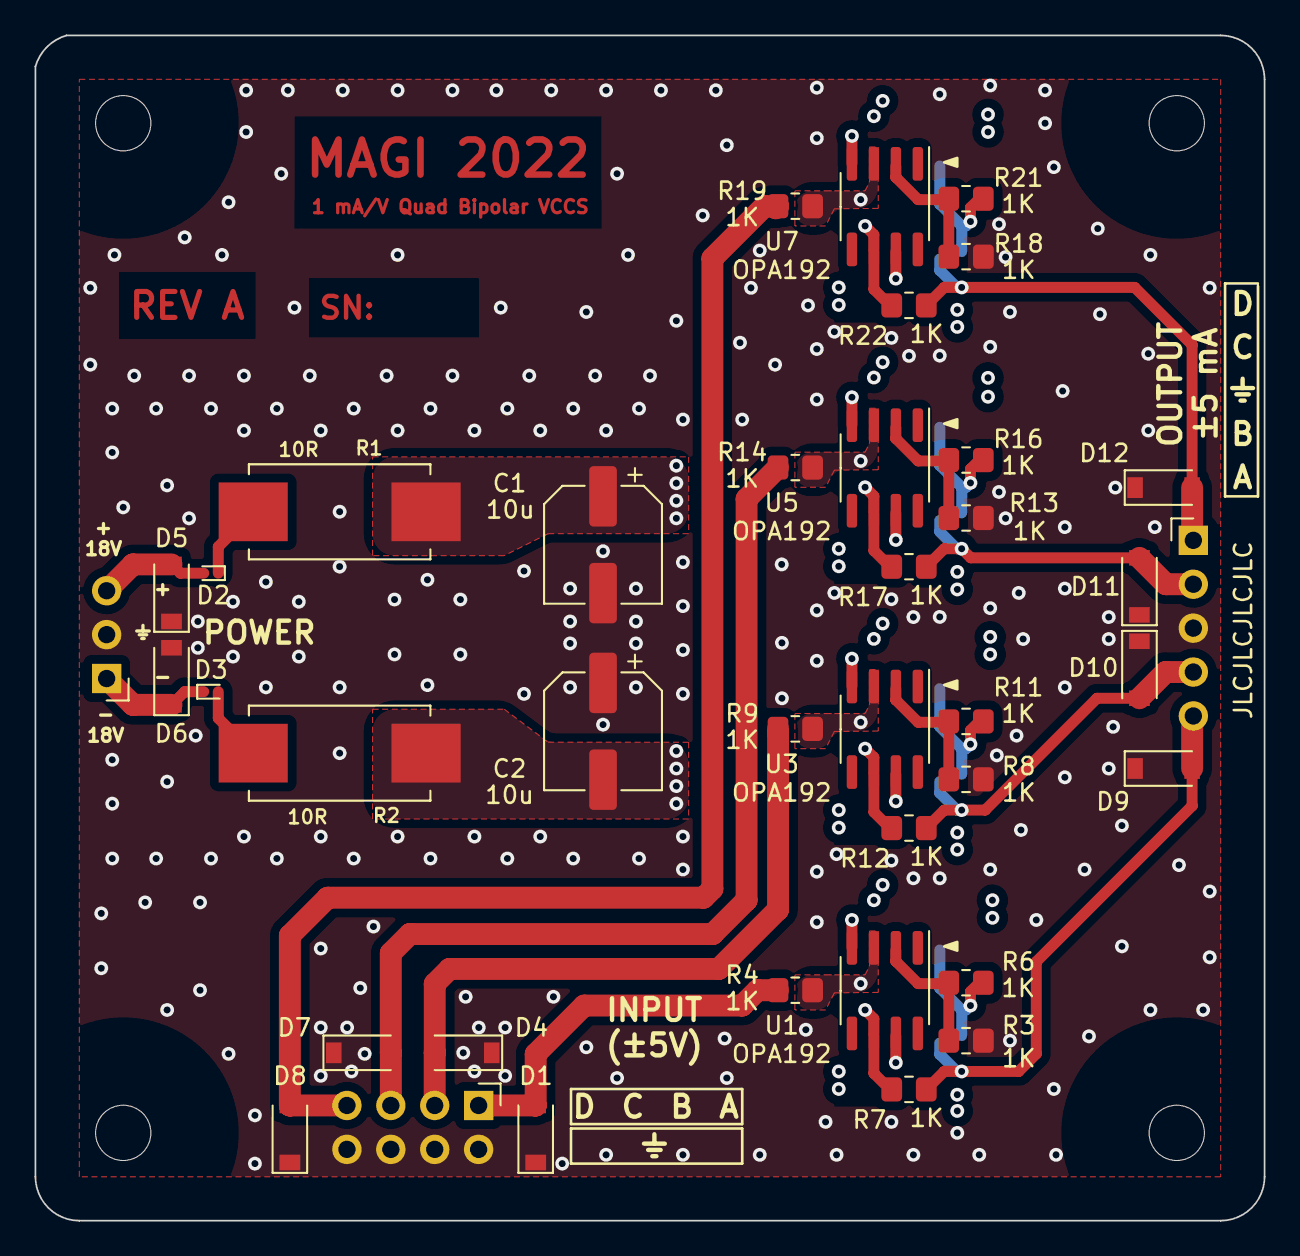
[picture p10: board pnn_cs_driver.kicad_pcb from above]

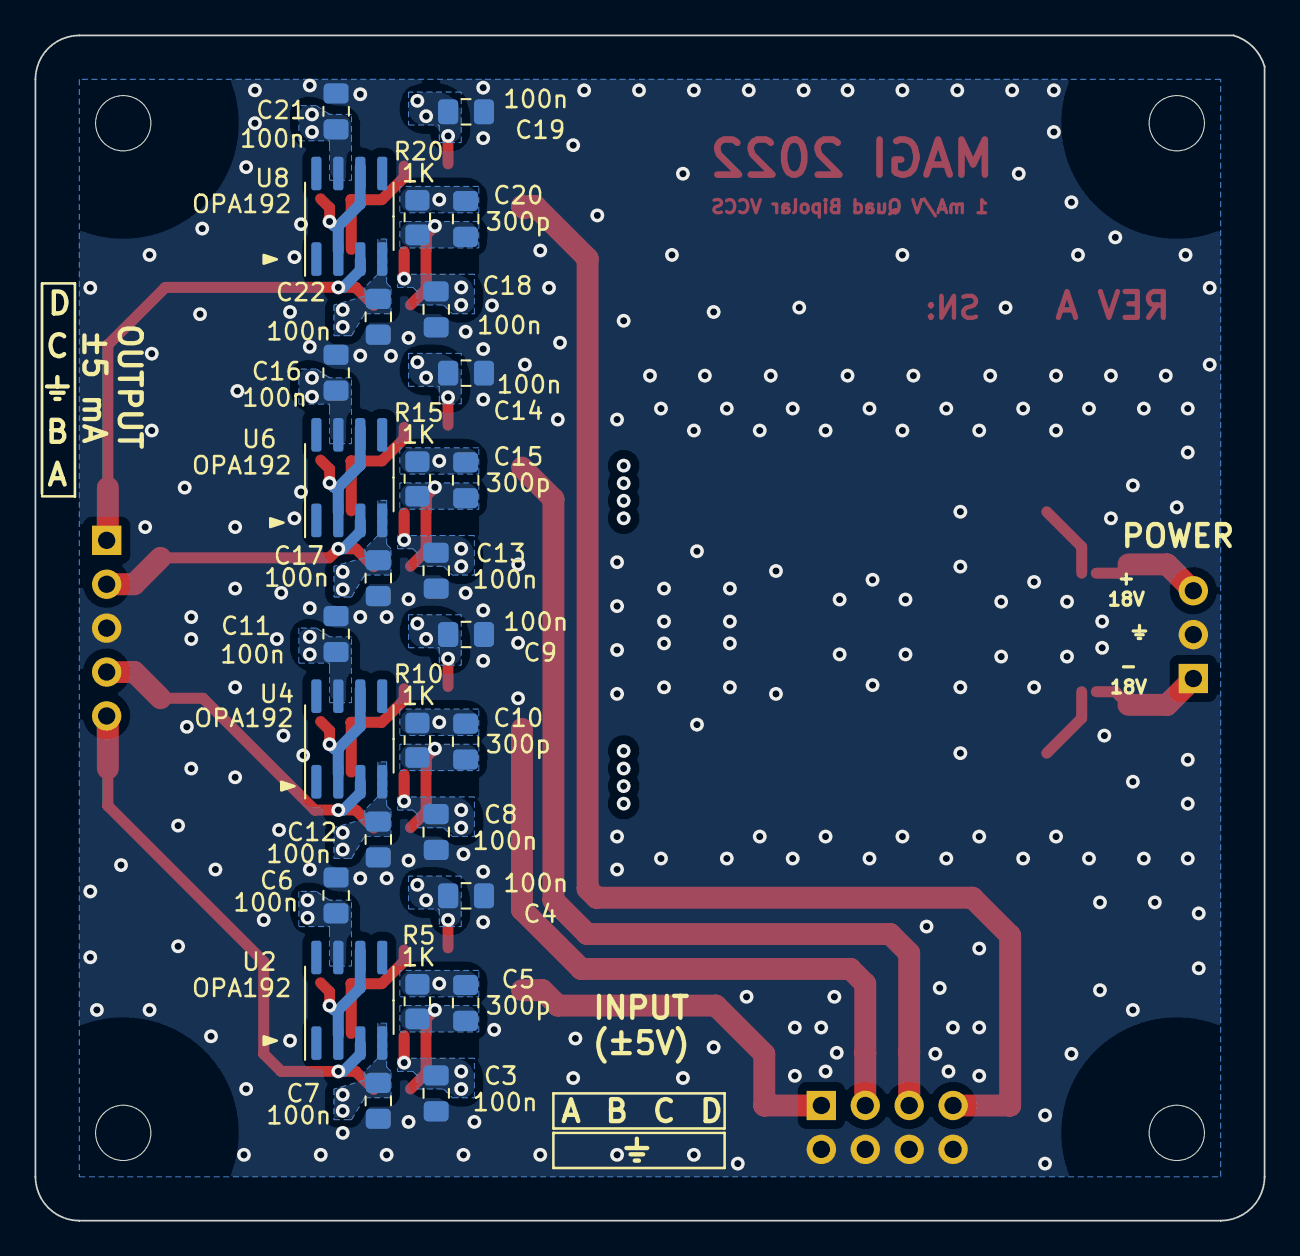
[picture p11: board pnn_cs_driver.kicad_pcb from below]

Board: 4 copper layers, 71.1 x 68.6 mm, 71 parts (28 on the bottom side), 31 nets.

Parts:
C1, C2: 10u; CP_Elec_6.3x5.9
C3, C4, C6, C7, C8, C9, C11, C12, C13, C14, C16, C17, C18, C19, C21, C22: 100n; C_0805_2012Metric_Pad1.18x1.45mm_HandSolder
C5, C10, C15, C20: 300p; C_0805_2012Metric_Pad1.18x1.45mm_HandSolder
D1, D4, D5, D6, D7, D8, D9, D10, D11, D12: TVS; D_SOD-123
D2, D3: D_Schottky; D_SOD-923
H1, H2, H3, H4: MountingHole; MountingHole_3.2mm_M3_ISO7380
J1: POWER; PinHeader_1x03_P2.54mm_Horizontal
J2: Conn_02x04_Odd_Even; PinHeader_2x04_P2.54mm_Horizontal
J3: OUTPUT; PinHeader_1x05_P2.54mm_Horizontal
R1, R2: 10R; wirewound_inrush_fp
R3, R4, R5, R6, R7, R8, R9, R10, R11, R12, R13, R14, R15, R16, R17, R18, R19, R20, R21, R22: 1K; R_0805_2012Metric_Pad1.20x1.40mm_HandSolder
U1, U2, U3, U4, U5, U6, U7, U8: OPA192; SOIC-8_3.9x4.9mm_P1.27mm

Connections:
+18V: C1.1, C3.2, C6.2, C8.2, C11.2, C13.2, C16.2, C18.2, C21.2, R1.1, U1.7 (V+), U2.7 (V+), U3.7 (V+), U4.7 (V+), U5.7 (V+), U6.7 (V+), U7.7 (V+), U8.7 (V+)
-18V: C2.2, C4.2, C7.2, C9.2, C12.2, C14.2, C17.2, C19.2, C22.2, R2.1, U1.4 (V-), U2.4 (V-), U3.4 (V-), U4.4 (V-), U5.4 (V-), U6.4 (V-), U7.4 (V-), U8.4 (V-)
GND: C1.2, C2.1, C3.1, C4.1, C6.1, C7.1, C8.1, C9.1, C11.1, C12.1, C13.1, C14.1, C16.1, C17.1, C18.1, C19.1, C21.1, C22.1, D1.1 (A1), D4.1 (A1), D5.1 (A1), D6.2 (A2), D7.1 (A1), D8.1 (A1), D9.1 (A1), D10.1 (A1), D11.1 (A1), D12.1 (A1), J1.2, J2.2, J2.4, J2.6, J2.8, J3.3, R3.1, R8.1, R13.1, R18.1
IN_A: D1.2 (A2), J2.1, R4.1
IN_B: D4.2 (A2), J2.3, R9.1
IN_C: D7.2 (A2), J2.5, R14.1
IN_D: D8.2 (A2), J2.7, R19.1
unnamed: C5.1, R4.2, R5.1, U1.3 (+)
unnamed: C5.2, R5.2, R7.1, U1.6
unnamed: C10.1, R9.2, R10.1, U3.3 (+)
unnamed: C10.2, R10.2, R12.1, U3.6
unnamed: C15.1, R14.2, R15.1, U5.3 (+)
unnamed: C15.2, R15.2, R17.1, U5.6
unnamed: C20.1, R19.2, R20.1, U7.3 (+)
unnamed: C20.2, R20.2, R22.1, U7.6
unnamed: D2.2 (A), D5.2 (A2), J1.3
unnamed: D3.1 (K), D6.1 (A1), J1.1
unnamed: D2.1 (K), R1.2
unnamed: D3.2 (A), R2.2
unnamed: R3.2, R6.1, U1.2 (-)
unnamed: R6.2, U2.2 (-), U2.6
unnamed: R8.2, R11.1, U3.2 (-)
unnamed: R11.2, U4.2 (-), U4.6
unnamed: R13.2, R16.1, U5.2 (-)
unnamed: R16.2, U6.2 (-), U6.6
unnamed: R18.2, R21.1, U7.2 (-)
unnamed: R21.2, U8.2 (-), U8.6
OUT_A: D9.2 (A2), J3.5, R7.2, U2.3 (+)
OUT_B: D10.2 (A2), J3.4, R12.2, U4.3 (+)
OUT_C: D11.2 (A2), J3.2, R17.2, U6.3 (+)
OUT_D: D12.2 (A2), J3.1, R22.2, U8.3 (+)

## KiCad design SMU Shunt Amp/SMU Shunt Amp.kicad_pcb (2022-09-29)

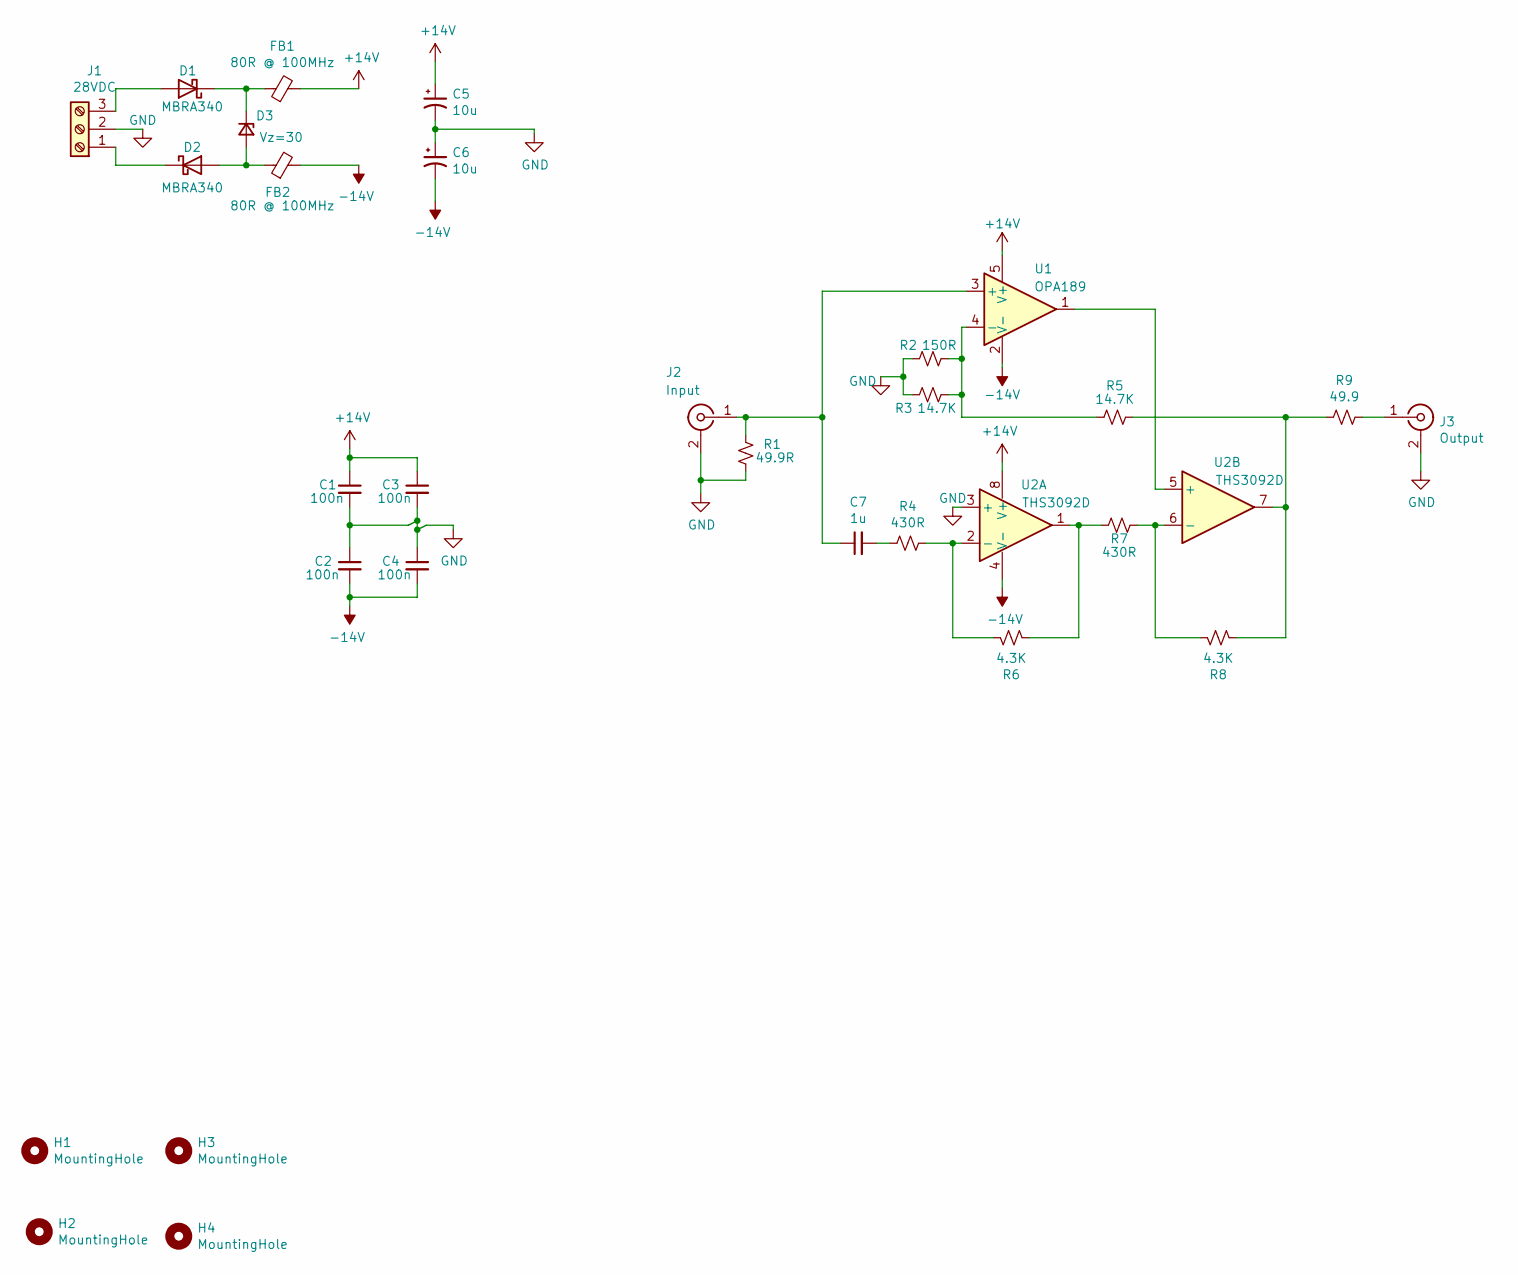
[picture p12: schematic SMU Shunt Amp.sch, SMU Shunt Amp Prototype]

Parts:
C1, C2, C3, C4: 100n; C_0805_2012Metric_Pad1.18x1.45mm_HandSolder; Part C0805C103K5GEC7210
C5, C6: 10u; CP_Elec_6.3x7.7; Part UCZ1J100MCS1GS
C7: 1u; C_0805_2012Metric_Pad1.18x1.45mm_HandSolder
D1, D2: MBRA340; D_SMA_Handsoldering
D3: Vz=30; D_SOD-123
FB1, FB2: 80R @ 100MHz; R_1206_3216Metric_Pad1.30x1.75mm_HandSolder
H1, H2, H3, H4: MountingHole; MountingHole_3.2mm_M3
J1: 28VDC; TerminalBlock_Phoenix_PT-1,5-3-5.0-H_1x03_P5.00mm_Horizontal
J2: Input; TE_1-1337445-0; Part 1-1337445-0
J3: Output; TE_1-1337445-0; Part 1-1337445-0
R1: 49.9R; R_0805_2012Metric_Pad1.20x1.40mm_HandSolder; Part CRCW080549R9FKEA
R2: 150R; R_0805_2012Metric_Pad1.20x1.40mm_HandSolder
R3, R5: 14.7K; R_0805_2012Metric_Pad1.20x1.40mm_HandSolder
R4, R7: 430R; R_0805_2012Metric_Pad1.20x1.40mm_HandSolder
R6, R8: 4.3K; R_0805_2012Metric_Pad1.20x1.40mm_HandSolder
R9: 49.9; R_0805_2012Metric_Pad1.20x1.40mm_HandSolder; Part CRCW080549R9FKEA
U1: OPA189; SOT-23-5_HandSoldering; Part OPA189IDBVR
U2: THS3092D; SOIC-8_3.9x4.9mm_P1.27mm

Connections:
+15V: C1.1, C3.1, C5.1, FB1.2, U1.5 (V+), U2.8 (V+)
-15V: C2.2, C4.2, C6.2, FB2.2, U1.2 (V-), U2.4 (V-)
GND: C1.2, C2.1, C3.2, C4.1, C5.2, C6.1, J1.2, J2.2 (Ext), J3.2 (Ext), R1.1, R2.2, R3.2, U2.3 (+)
unnamed: C7.1, J2.1 (In), R1.2, U1.3 (+)
unnamed: C7.2, R4.2
unnamed: D1.1 (K), D3.1 (K), FB1.1
unnamed: D1.2 (A), J1.3
unnamed: D2.1 (K), J1.1
unnamed: D2.2 (A), D3.2 (A), FB2.1
unnamed: J3.1 (In), R9.1
unnamed: R2.1, R3.1, R5.2, U1.4 (-)
unnamed: R4.1, R6.2, U2.2 (-)
unnamed: R5.1, R8.1, R9.2, U2.7
unnamed: R6.1, R7.2, U2.1
unnamed: R7.1, R8.2, U2.6 (-)
unnamed: U1.1, U2.5 (+)

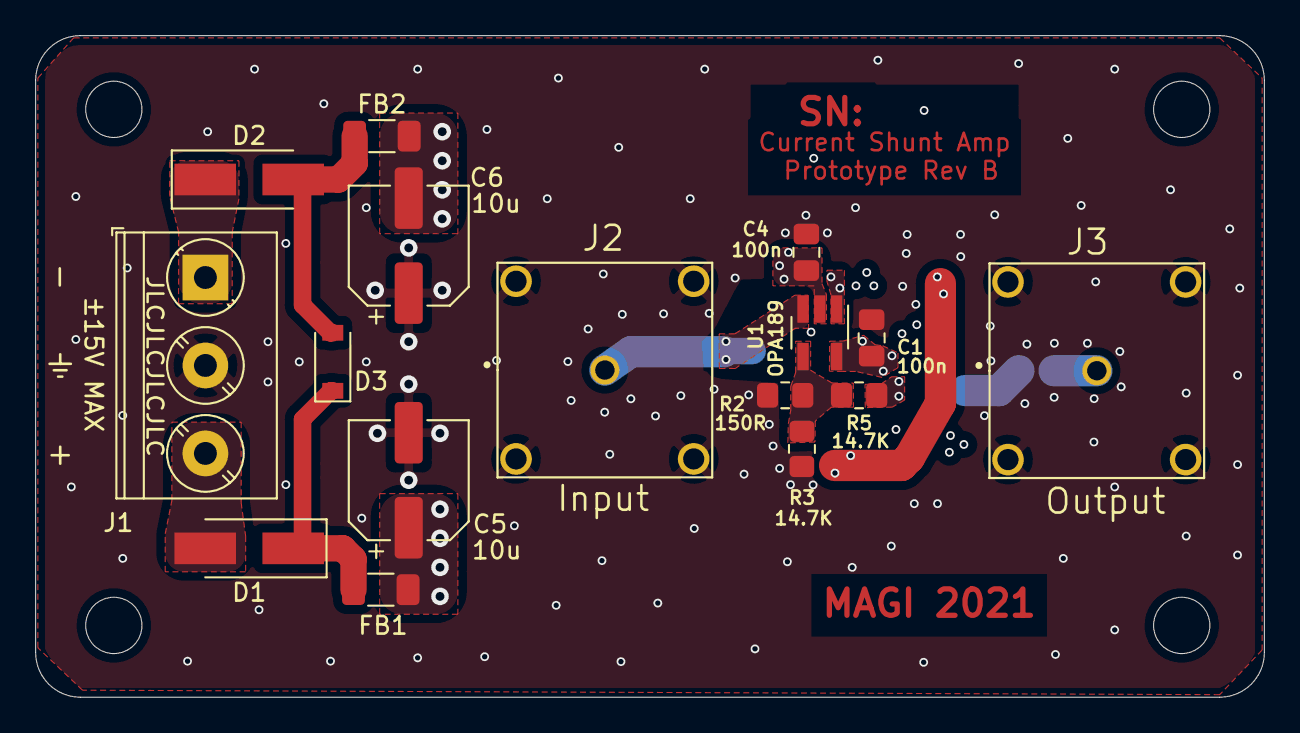
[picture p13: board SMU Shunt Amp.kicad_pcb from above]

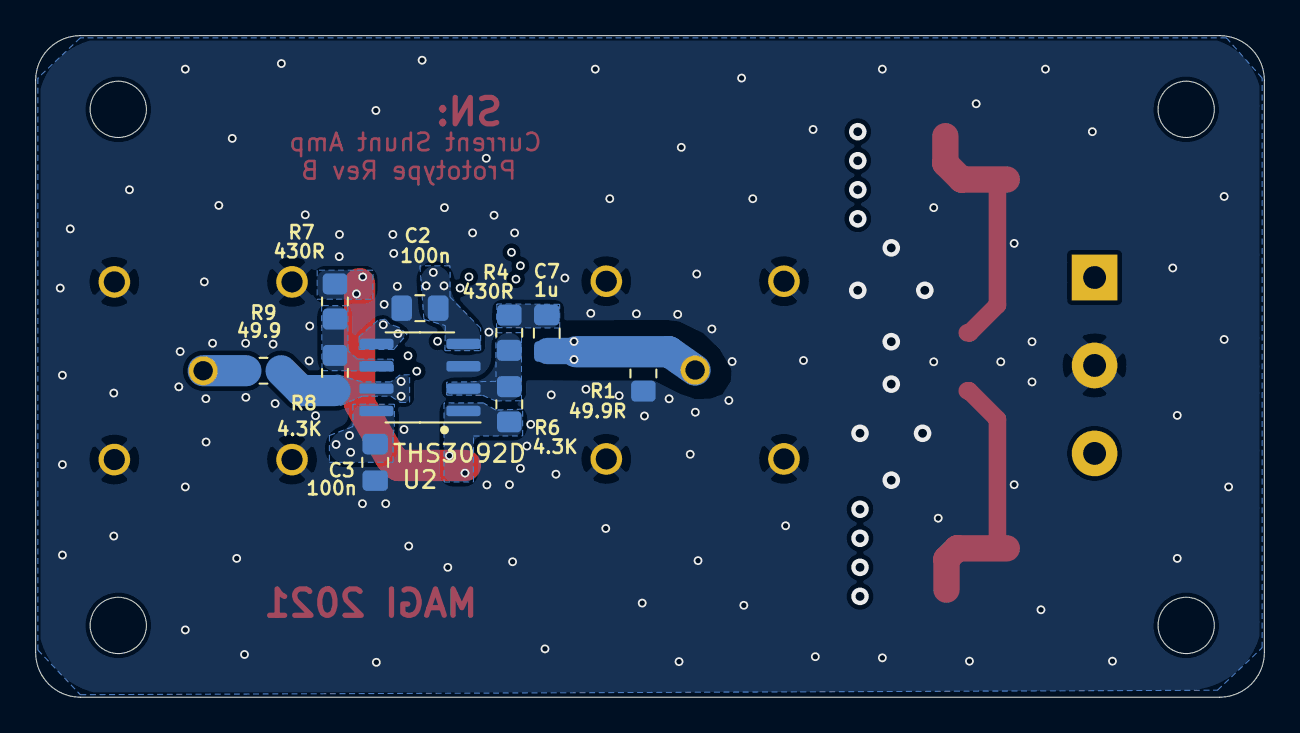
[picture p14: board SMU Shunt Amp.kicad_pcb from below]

Board: 4 copper layers, 69.9 x 37.6 mm, 30 parts (10 on the bottom side), 16 nets.

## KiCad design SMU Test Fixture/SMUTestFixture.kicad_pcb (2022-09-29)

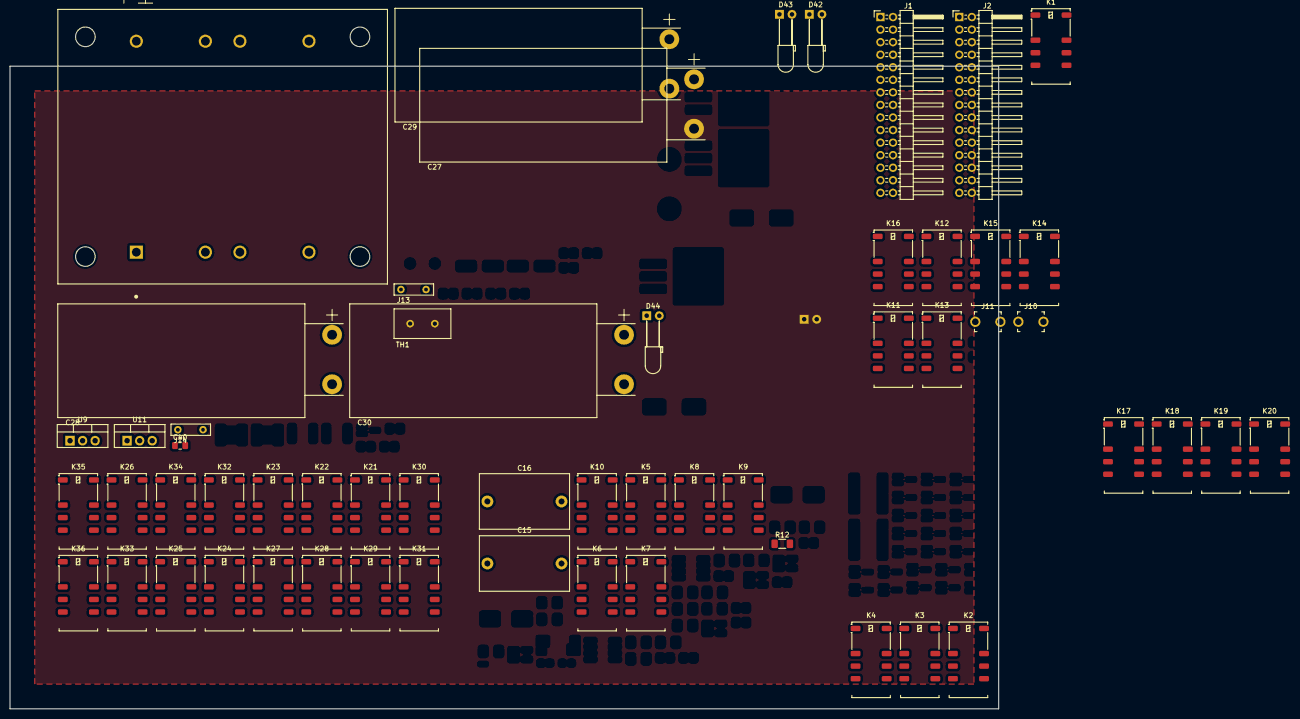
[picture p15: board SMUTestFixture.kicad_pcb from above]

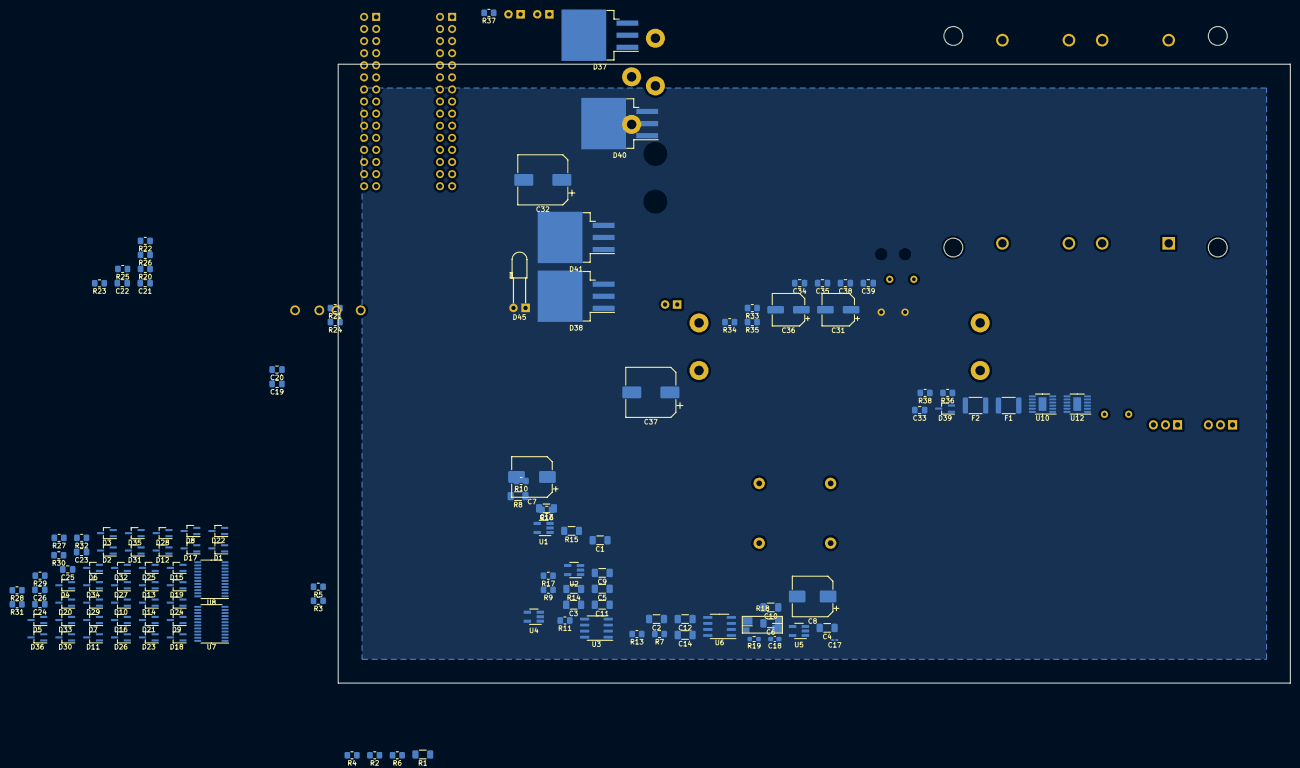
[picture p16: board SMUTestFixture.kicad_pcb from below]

Board: 2 copper layers, 200.0 x 130.0 mm, 181 parts (124 on the bottom side), 121 nets, no tracks yet.

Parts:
C1, C2, C3, C4, C5, C6, C9, C10, C11, C12, C13, C14: 100n; C_1206_3216Metric_Pad1.33x1.80mm_HandSolder
C7, C8: 100u; CP_Elec_8x10
C15, C16: 1u; C_Rect_L18.0mm_W11.0mm_P15.00mm_FKS3_FKP3
C17: 33p; C_0201_0603Metric_Pad0.64x0.40mm_HandSolder
C18: 6.2p; C_0603_1608Metric_Pad1.08x0.95mm_HandSolder
C19, C20, C21, C22: C_Small; C_0805_2012Metric_Pad1.18x1.45mm_HandSolder
C23, C24, C25, C26, C33, C39: 10u; C_0805_2012Metric_Pad1.18x1.45mm_HandSolder
C27, C28, C29, C30: 4.7m; d=22_L=50_Radial_Horiz_P=10
C31, C36: 10u; CP_Elec_6.3x5.8
C32, C37: 150u; CP_Elec_10x10
C34, C40: 4.7u; C_0805_2012Metric_Pad1.18x1.45mm_HandSolder
C35, C38: 22u; C_0805_2012Metric_Pad1.18x1.45mm_HandSolder
D1, D2, D3, D4, D5, D6, D7, D8, D9, D10, D11, D12, D13, D14, D15, D16, D17, D18, D19, D20, D21, D22, D23, D24, D25, D26, D27, D28, D29, D30, D31, D32, D33, D34, D35, D36: Vz=+-15V; SOT-323_SC-70_Handsoldering
D37, D38, D40, D41: D; TO-263-3_TabPin2
D39: 20V Clamp; SOT-323_SC-70_Handsoldering
D42, D43, D44, D45: LED; LED_D3.0mm_Horizontal_O6.35mm_Z2.0mm
F1, F2: 1 A; Fuse_1812_4532Metric
J1, J2: AD2 Connector; PinHeader_2x15_P2.54mm_Horizontal
J10, J11: 105-1102-001; Test_Jack_Horiz
J13: Hot_Spade; p250_spade
J14: Neutral_Spade; p250_spade
K1: External Source Enable; Relay_DPDT_Kemet_EE2_NUH
K2, K3, K4, K21, K22, K23, K24, K25, K26, K27, K28, K29, K30, K31, K32, K33, K34, K35, K36: EC2-12SNU; Relay_DPDT_Kemet_EE2_NUH
K5: Integrator Reset; Relay_DPDT_Kemet_EE2_NUH
K6: I/V Mode Select; Relay_DPDT_Kemet_EE2_NUH
K7: 3x Gain Enable; Relay_DPDT_Kemet_EE2_NUH
K8: Shunt Select; Relay_DPDT_Kemet_EE2_NUH
K9: Shunt/Sense Select; Relay_DPDT_Kemet_EE2_NUH
K10: Sense Select; Relay_DPDT_Kemet_EE2_NUH
K11: 50 Ohm Ena; Relay_DPDT_Kemet_EE2_NUH
K12: Single/Diff Switch; Relay_DPDT_Kemet_EE2_NUH
K13: AC/DC Couple; Relay_DPDT_Kemet_EE2_NUH
K14: AC/DC Couple A; Relay_DPDT_Kemet_EE2_NUH
K15: Ext Meas Sel B; Relay_DPDT_Kemet_EE2_NUH
K16: Ext Meas Sel A; Relay_DPDT_Kemet_EE2_NUH
K17: 6x1 Mux Sel A; Relay_DPDT_Kemet_EE2_NUH
K18: 6x1 Mux Sel B; Relay_DPDT_Kemet_EE2_NUH
K19, K20: 6x1 Mux Sel C; Relay_DPDT_Kemet_EE2_NUH
R1, R8, R12: 1M; R_1206_3216Metric_Pad1.30x1.75mm_HandSolder
R2: 100K; R_0805_2012Metric_Pad1.20x1.40mm_HandSolder
R3, R17: 10K; R_0805_2012Metric_Pad1.20x1.40mm_HandSolder
R4: 1K; R_0805_2012Metric_Pad1.20x1.40mm_HandSolder
R5: 100R; R_0805_2012Metric_Pad1.20x1.40mm_HandSolder
R6, R16: 10R; R_0805_2012Metric_Pad1.20x1.40mm_HandSolder
R7, R10: 5K; R_0805_2012Metric_Pad1.20x1.40mm_HandSolder
R9: 56K; R_0805_2012Metric_Pad1.20x1.40mm_HandSolder
R11: 11.8K; R_0805_2012Metric_Pad1.20x1.40mm_HandSolder
R13: 5.9K; R_0805_2012Metric_Pad1.20x1.40mm_HandSolder
R14, R15: 14.7K; R_1206_3216Metric_Pad1.30x1.75mm_HandSolder
R18: 0R01; CSM_Vishay_Shunt_4term
R19: 150R; R_0603_1608Metric_Pad0.98x0.95mm_HandSolder
R20, R21, R22: 49.9R; R_0805_2012Metric_Pad1.20x1.40mm_HandSolder
R23, R24, R25, R26: 27M; R_0805_2012Metric_Pad1.20x1.40mm_HandSolder
R27: 2.430K; R_0805_2012Metric_Pad1.20x1.40mm_HandSolder
R28, R30, R31, R32: 270; R_0805_2012Metric_Pad1.20x1.40mm_HandSolder
R29: 1.150K; R_0805_2012Metric_Pad1.20x1.40mm_HandSolder
R33: 270R; R_0805_2012Metric_Pad1.20x1.40mm_HandSolder
R34, R38: 750R; R_0805_2012Metric_Pad1.20x1.40mm_HandSolder
R35, R37: 150k; R_0805_2012Metric_Pad1.20x1.40mm_HandSolder
R36: 620R; R_0805_2012Metric_Pad1.20x1.40mm_HandSolder
T1: VPP28-1060; XFMR_VPP28-1060
TH1: 3.5A max <130C; NTC d=11.5 p=5mm w=6mm
U1, U4: OPA192; SOT-23-5_HandSoldering
U2, U5: OPA189; SOT-23-5_HandSoldering
U3: OPA551U; SOIC-8_3.9x4.9mm_P1.27mm
U6: OPA1611; SOIC-8_3.9x4.9mm_P1.27mm
U7, U8: ADG1414BRU; TSSOP-24_4.4x7.8mm_P0.65mm
U9: LT1086-5.0; TO-220-3_Vertical
U10: LT3045xMSE-1; MSOP-12-1EP_3x4mm_P0.65mm_EP1.65x2.85mm
U11: LT1086-12; TO-220-3_Vertical
U12: LT3094xMSE; MSOP-12-1EP_3x4mm_P0.65mm_EP1.65x2.85mm

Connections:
3x_gain_en_r: D1.3, D2.3, D3.3, D4.3, D5.3, D6.3, K1.12, K2.12, K3.12, K4.12, K7.12, K8.12, U8.5
3x_gain_en_s: D2.2, D8.2, D14.2, D20.2, D26.2, D32.2, K7.1, K11.1, K17.1, K23.1, K29.1, K35.1, U7.14
+3V8: R27.2, R29.1, U7.23, U8.23
+5V: C32.1, D42.2, U9.2
+12V: C37.1, D44.2, R27.1, R28.2, R31.2, U11.2
+15V: C1.1, C2.1, C3.1, C4.1, C5.1, C6.1, C7.1, C23.1, C24.1, C33.1, D43.2, U1.4, U2.4, U3.7, U4.4, U5.4, U6.4, U7.2, U8.2, U10.10, U10.11
-15V: C8.2, C9.2, C10.2, C11.2, C12.2, C13.2, C14.2, C25.2, C26.2, C39.2, D45.1, U1.5, U2.5, U3.1, U3.4, U3.5, U4.5, U5.5, U6.5, U7.21, U8.21, U12.10, U12.11, U12.12
/Ammeter and Charge Integrator/IV_src_output: K1.5, U3.6
/Ammeter and Charge Integrator/ammeter_input: K9.4, R1.1, R2.1, R3.1, R4.1, R5.1, R6.1
/Ammeter and Charge Integrator/ammeter_meas_output: C18.1, K17.8, R12.2, R15.1, U6.3
/Ammeter and Charge Integrator/ammeter_output: K6.10, K8.8, K10.8, K20.3, K21.8, K22.8, K23.8, K24.8, K25.8, K26.8, K27.8, K28.8, K29.8, K30.8, K31.8, K32.8, K33.8, K34.8, K35.8, K36.8, R8.2, R16.2, R17.2, R18.3, R18.4
/Ammeter and Charge Integrator/charge_int_output: C16.1, K17.10, R10.2, U4.3
/DIO_0: J1.15, J2.15, U7.3
/DIO_1: J1.13, J2.13, U7.1, U8.1
/DIO_2: J1.11, J2.11, U7.24, U8.24
/DIO_3: J1.9, J2.9
/DIO_4: J1.7, J2.7
/DIO_5: J1.5, J2.5
/DIO_6: J1.3, J2.3
/DIO_7: J1.1, J2.1
/DIO_8: J1.16, J2.16
/DIO_9: J1.14, J2.14
/DIO_10: J1.12, J2.12
/DIO_11: J1.10, J2.10
/DIO_12: J1.8, J2.8
/DIO_13: J1.6, J2.6
/DIO_14: J1.4, J2.4
/DIO_15: J1.2, J2.2
/Impedance Analyzer/impa_input: K1.4, K4.4, K17.3
/Power Supplies/unreg_neg_18VDC: C29.2, C30.2, C40.2, D39.2, D40.2, D41.2, U12.1, U12.2, U12.3, U12.5, U12.13
/Power Supplies/unreg_pos_18VDC: C27.1, C28.1, C31.1, C34.1, C36.1, D37.1, D38.1, D39.1, U9.3, U10.1, U10.4, U10.7, U11.3
/Relay Driver/sd_a_to_b: U7.22, U8.3
/Scope Meas Selector/input_2a: C15.1, K17.5, R7.2, U1.3
/ad2_cal_scope_p: K16.9, K19.8, K20.8
/ext_meas_dut: C22.2, J1.27, K14.8, K15.3, K20.4, K20.9
/ext_meas_phiqi: C21.2, J1.29, K14.5, K15.5, K19.4, K19.9
/ext_source: K1.3, R21.2
/ps_n: J1.24, J2.24
/ps_p: J1.23, J2.23
/scope_1_n: C19.2, J1.30, K12.4, K13.5
/scope_2_n: C20.2, J1.28, K12.9, K13.8
/trig_1: J1.17, J2.17
/trig_2: J1.18, J2.18
/wg_1: J1.21, K11.5, K15.8, K16.8, R9.1, R20.2, U2.1
/wg_2: J1.22, K11.8, K15.10, R22.2
GND: C1.2, C2.2, C3.2, C4.2, C5.2, C6.2, C7.2, C8.1, C9.1, C10.1, C11.1, C12.1, C13.1, C14.1, C17.2, C23.2, C24.2, C25.1, C26.1, C27.2, C28.2, C29.1, C30.1, C31.2, C32.2, C33.2, C34.2, C35.2, C36.2, C37.2, C38.1, C39.1, C40.1, D39.3, J1.19, J1.20, J1.25, J1.26, J2.19, J2.20, J2.25, J2.26, J11.1, K12.5, K12.8, K16.10, K21.5, K22.5, K23.5, K24.5, K25.5, K26.5, K27.5, K28.5, K29.5, K30.5, K31.5, K32.5, K33.5, K34.5, K35.5, K36.5, R9.2, R13.2, R14.2, R19.2, R23.2, R24.2, R25.2, R26.2, R29.2, R30.2, R32.2, R33.2, R34.2, R35.2, R36.2, R37.1, R38.1, T1.12, U1.1, U4.1, U6.2, U7.4, U8.4, U9.1, U10.6, U10.9, U11.1, U12.6, U12.9
unnamed: C15.2, K5.3, R8.1, U1.2
unnamed: C16.2, K5.10, R12.1, U4.2
unnamed: C17.1, K7.4, R11.1, U2.2, U3.2
unnamed: C18.2, R14.1, R15.2, R19.1, U5.2
unnamed: C19.1, K13.3
unnamed: C20.1, K13.10
unnamed: C21.1, K14.3
unnamed: C22.1, K14.10
unnamed: C35.1, R35.1, U10.8
unnamed: C38.2, R37.2, U12.8
unnamed: D37.2, D40.1, F1.1
unnamed: D38.2, D41.1, F2.1
unnamed: D42.1, R33.1
unnamed: D43.1, R34.1
unnamed: D44.1, R36.1
unnamed: D45.2, R38.2
unnamed: F1.2, T1.7, T1.10
unnamed: F2.2, T1.9
unnamed: K13.4, R23.1
unnamed: K13.9, R24.1
unnamed: K14.4, R25.1
unnamed: J10.1, K16.4
unnamed: K14.9, R26.1
unnamed: J13.1, TH1.2
unnamed: J14.1, T1.3, T1.6
unnamed: K2.3, R1.2
unnamed: K2.4, K3.3
unnamed: K2.5, R2.2
unnamed: K2.8, R4.2
unnamed: K2.9, K3.5
unnamed: K2.10, R3.2
unnamed: K3.4, K4.3
unnamed: K3.8, R6.2
unnamed: K3.9, K4.5
unnamed: K3.10, R5.2
unnamed: K5.4, K5.5, R7.1
unnamed: K5.8, K5.9, R10.1
unnamed: K6.8, K9.9, U5.1
unnamed: K6.9, R11.2
unnamed: K7.5, R13.1
unnamed: K8.3, R18.1
unnamed: K8.4, K9.3
unnamed: K8.9, K9.5
unnamed: K10.3, R18.2
unnamed: K9.10, K10.4
unnamed: K8.5, K10.5, R16.1
unnamed: K9.8, K10.9
unnamed: K8.10, K10.10, R17.1
unnamed: K11.3, R20.1
unnamed: K11.10, R22.1
unnamed: K15.4, K16.3
unnamed: K15.9, K16.5
unnamed: K17.4, K18.3
unnamed: K17.9, K18.5
unnamed: K18.4, K19.3
unnamed: K18.9, K19.5
unnamed: R28.1, U7.18
unnamed: R30.1, U7.20
unnamed: R31.1, U8.18
unnamed: R32.1, U8.20
unnamed: T1.1, T1.4, TH1.1
unnamed: U2.3, U3.3
unnamed: U5.3, U6.1
unnamed: U7.6, U7.8, U7.10, U7.12, U7.13, U7.15, U7.17, U7.19
unnamed: U8.6, U8.8, U8.10, U8.12, U8.13, U8.15, U8.17, U8.19
cur_volt_mode_sel_r: D7.3, D8.3, D9.3, D10.3, D11.3, D12.3, K5.12, K6.12, K9.12, K10.12, K11.12, K15.12, U8.7
cur_volt_mode_sel_s: D5.2, D11.2, D17.2, D23.2, D29.2, D35.2, K4.1, K6.1, K12.1, K20.1, K26.1, K32.1, U7.7
dut_sel_1_r: D19.3, D20.3, D21.3, D22.3, D23.3, D24.3, K19.12, K20.12, K21.12, K22.12, K23.12, K24.12, U8.11
dut_sel_10_r: D25.3, D26.3, D27.3, D28.3, D29.3, D30.3, K25.12, K26.12, K27.12, K28.12, K29.12, K30.12, U8.14
dut_sel_10_s: D1.2, D7.2, D13.2, D19.2, D25.2, D31.2, K8.1, K15.1, K18.1, K24.1, K30.1, K36.1, U7.16
dut_sel_11_r: D31.3, D32.3, D33.3, D34.3, D35.3, D36.3, K31.12, K32.12, K33.12, K34.12, K35.12, K36.12, U8.16
dut_sel_11_s: D6.2, D12.2, D18.2, D24.2, D30.2, D36.2, K1.1, K9.1, K16.1, K19.1, K25.1, K31.1, U7.5
dut_sel_13_s: D4.2, D10.2, D16.2, D22.2, D28.2, D34.2, K3.1, K10.1, K13.1, K21.1, K27.1, K33.1, U7.9
dut_sel_14_s: D3.2, D9.2, D15.2, D21.2, D27.2, D33.2, K2.1, K5.1, K14.1, K22.1, K28.1, K34.1, U7.11
ext_acdc_n_r: D13.3, D14.3, D15.3, D16.3, D17.3, D18.3, K12.12, K13.12, K14.12, K16.12, K17.12, K18.12, U8.9

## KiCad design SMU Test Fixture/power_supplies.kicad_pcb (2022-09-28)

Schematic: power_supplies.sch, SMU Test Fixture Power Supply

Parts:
C27, C28, C29, C30: 510u; CP_Elec_18x22
C31, C37: 10u; CP_Elec_6.3x5.8
C32, C38: 150u; CP_Elec_10x10
C33, C39: 10u; C_0805_2012Metric_Pad1.18x1.45mm_HandSolder_Kelvin
C34, C40: 4.7u; C_0805_2012Metric_Pad1.18x1.45mm_HandSolder
C35, C36: 22u; C_0805_2012Metric_Pad1.18x1.45mm_HandSolder
C41: 1u 10V; C_0603_1608Metric_Pad1.08x0.95mm_HandSolder
D37, D38, D40, D41: D; TO-263-2
D42, D43, D44, D45: LED; LED_D3.0mm_Horizontal_O6.35mm_Z2.0mm
F1, F2: 3.7 A; Fuse_2920_7451Metric_Pad2.10x5.45mm_HandSolder
J13: Hot_Spade; p250_spade
J14: Power Outputs; PinHeader_1x05_P2.54mm_Horizontal
J15: Neutral_Spade; p250_spade
Q1: IRLR6225TRPBF; TO-252-2
Q2: NTD3055-150T4G; TO-252-2
Q3: MMBT3906; SOT-23
R33, R34: 750R; R_0805_2012Metric_Pad1.20x1.40mm_HandSolder
R35: 270R; R_0805_2012Metric_Pad1.20x1.40mm_HandSolder
R36: 620R; R_0805_2012Metric_Pad1.20x1.40mm_HandSolder
R37, R38: 150k; R_0805_2012Metric_Pad1.20x1.40mm_HandSolder
R39, R43, R51: 100R; R_0603_1608Metric_Pad0.98x0.95mm_HandSolder
R40: 2.55K; R_0603_1608Metric_Pad0.98x0.95mm_HandSolder
R41, R44: 10K; R_0603_1608Metric_Pad0.98x0.95mm_HandSolder
R42: 1.5K; R_0603_1608Metric_Pad0.98x0.95mm_HandSolder
R45: 21.5K; R_0603_1608Metric_Pad0.98x0.95mm_HandSolder
R46: 20K; R_0603_1608Metric_Pad0.98x0.95mm_HandSolder
R47: 2.43K; R_0603_1608Metric_Pad0.98x0.95mm_HandSolder
R48: 215K; R_0603_1608Metric_Pad0.98x0.95mm_HandSolder
R49: 600R; R_0603_1608Metric_Pad0.98x0.95mm_HandSolder
R50: 250K; R_0603_1608Metric_Pad0.98x0.95mm_HandSolder
R52: 10k; R_0603_1608Metric_Pad0.98x0.95mm_HandSolder
T1: VPP28-1060; XFMR_VPP28-1060
TH1: 2.5A max, 33R @ 25C; NTC d=15 p=7p5mm w=7mm
THJ1, THJ2: Thermal Jumper; C_0805_2012Metric_Pad1.18x1.45mm_HandSolder
U9: LT1086-5.0; TO-220-3_Vertical
U10: LT3045; MSOP-12-1EP_3x4mm_P0.65mm_EP1.65x2.85mm
U11: LT1086-12; TO-220-3_Vertical
U12: LT3094; MSOP-12-1EP_3x4mm_P0.65mm_EP1.65x2.85mm
U13: LTC2966CSWPBF; QFN-16-1EP_3x3mm_P0.5mm_EP1.45x1.45mm; MANUFACTURER_PART_NUMBER ltc2966csw#pbf

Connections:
+5V: C32.1, D44.2, J14.3, U9.2 (VO)
+12V: C31.1, C38.1, D45.2, J14.4, U9.3 (VI), U11.2 (VO)
+15V: C33.1, D42.2, J14.5, U10.10, U10.11, U10.12
-15V: C39.2, D43.1, J14.1, U12.10 (OUTS), U12.11 (OUT), U12.12 (OUT)
/neg_disable: Q2.1, R51.2
/ovp_ref: R40.1, R45.1, R49.1, U13.1, U13.4, U13.6, U13.9, U13.14
/pos_disable: Q1.1, R39.1
/unreg_neg_18VDC: C29.2, C30.2, C40.2, Q2.2, R48.2, R52.2, THJ1.1, THJ2.1, U12.1 (IN), U12.2 (IN), U12.3 (EN/UV), U12.5 (PGFB), U12.13 (IN)
/unreg_pos_18VDC: C27.1, C28.1, C34.1, C37.1, Q1.3, R41.2, R50.1, U10.1, U10.2, U10.7, U11.3 (VI), U13.15
GND: C27.2, C28.2, C29.1, C30.1, C31.2, C32.2, C33.2, C34.2, C35.2, C36.1, C37.2, C38.2, C39.1, C40.1, C41.2, J14.2, R33.2, R34.2, R35.2, R36.2, R37.2, R38.1, R44.1, R46.2, T1.12, THJ1.2, THJ2.2, U9.1 (GND), U10.6, U10.9, U10.13, U11.1 (GND), U12.6 (ILIM), U12.9 (GND), U13.5, U13.7, U13.8, U13.12, U13.17
unnamed: C35.1, R37.1, U10.8
unnamed: C36.2, R38.2, U12.8 (SET)
unnamed: C41.1, R49.2
unnamed: D37.1 (K), D38.1 (K), Q1.2
unnamed: D37.2 (A), D40.1 (K), F1.1
unnamed: D38.2 (A), D41.1 (K), F2.1
unnamed: D40.2 (A), D41.2 (A), Q2.3
unnamed: D42.1, R33.1
unnamed: D43.2, R34.1
unnamed: D44.1, R35.1
unnamed: D45.1, R36.1
unnamed: F1.2, T1.7, T1.10
unnamed: F2.2, T1.9
unnamed: J13.1, TH1.2
unnamed: J15.1, T1.3, T1.6
unnamed: Q3.1, R43.2
unnamed: Q3.2, R41.1, R44.2
unnamed: Q3.3, R51.1, R52.1
unnamed: R39.2, R50.2, U13.16
unnamed: R40.2, R42.1, U13.2
unnamed: R42.2, R46.1, U13.3
unnamed: R43.1, U13.13
unnamed: R45.2, R47.1, U13.11
unnamed: R47.2, R48.1, U13.10
unnamed: T1.1, T1.4, TH1.1

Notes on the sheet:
+ 15V for Analog Section
- 15V for Analog Section
+ 5V for Aux / pH Meter
+ 12 V for Relays
To BZH01/Z0000/01 Switchable, fused, power entry module 2.5A Slow Blow
Output Connector
Output Indicators
LT3045 bottom pad is input. Use thermal jumpers to conduct heat into ground.
Overvoltage Protection
High threshold: ±21.5 V Low threshold: ±20 V
Mains Input and Rectification

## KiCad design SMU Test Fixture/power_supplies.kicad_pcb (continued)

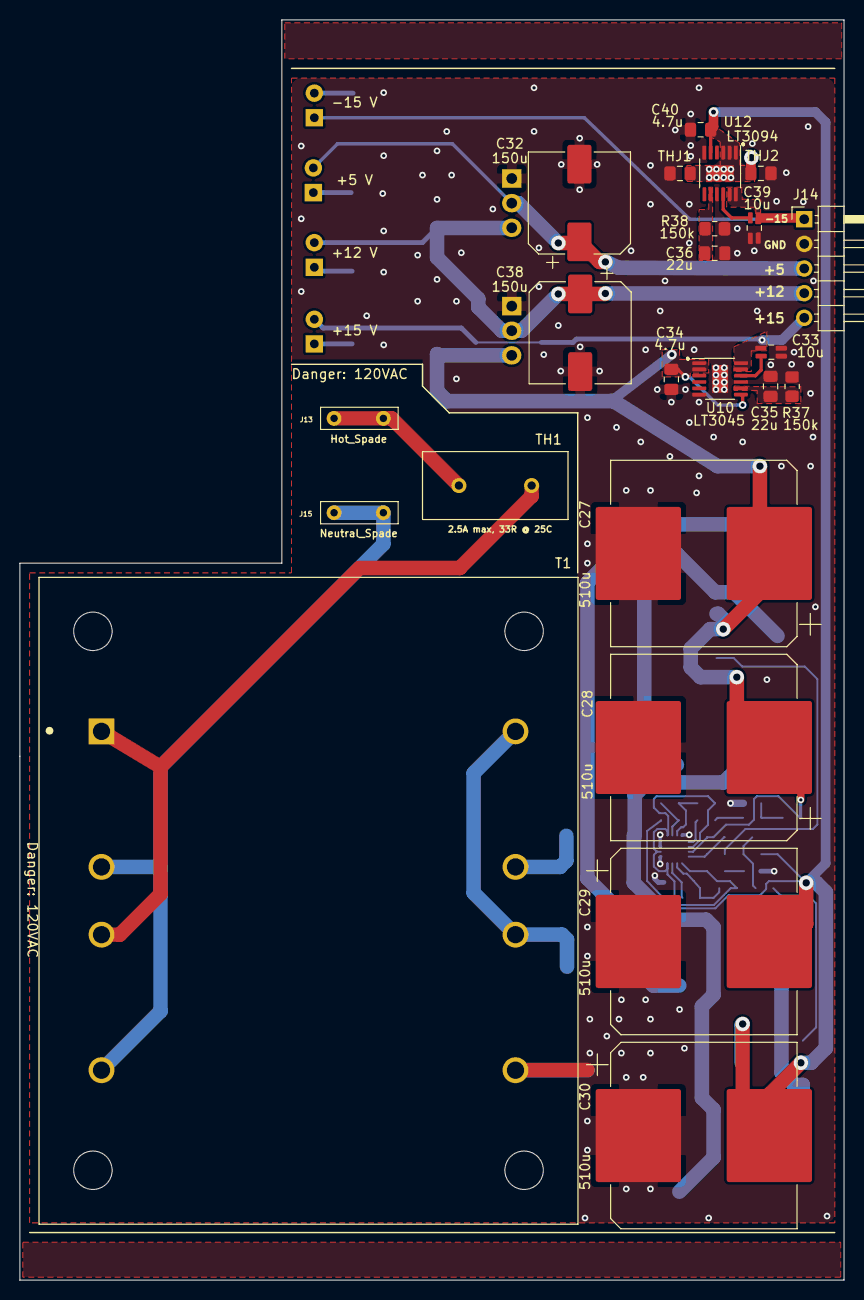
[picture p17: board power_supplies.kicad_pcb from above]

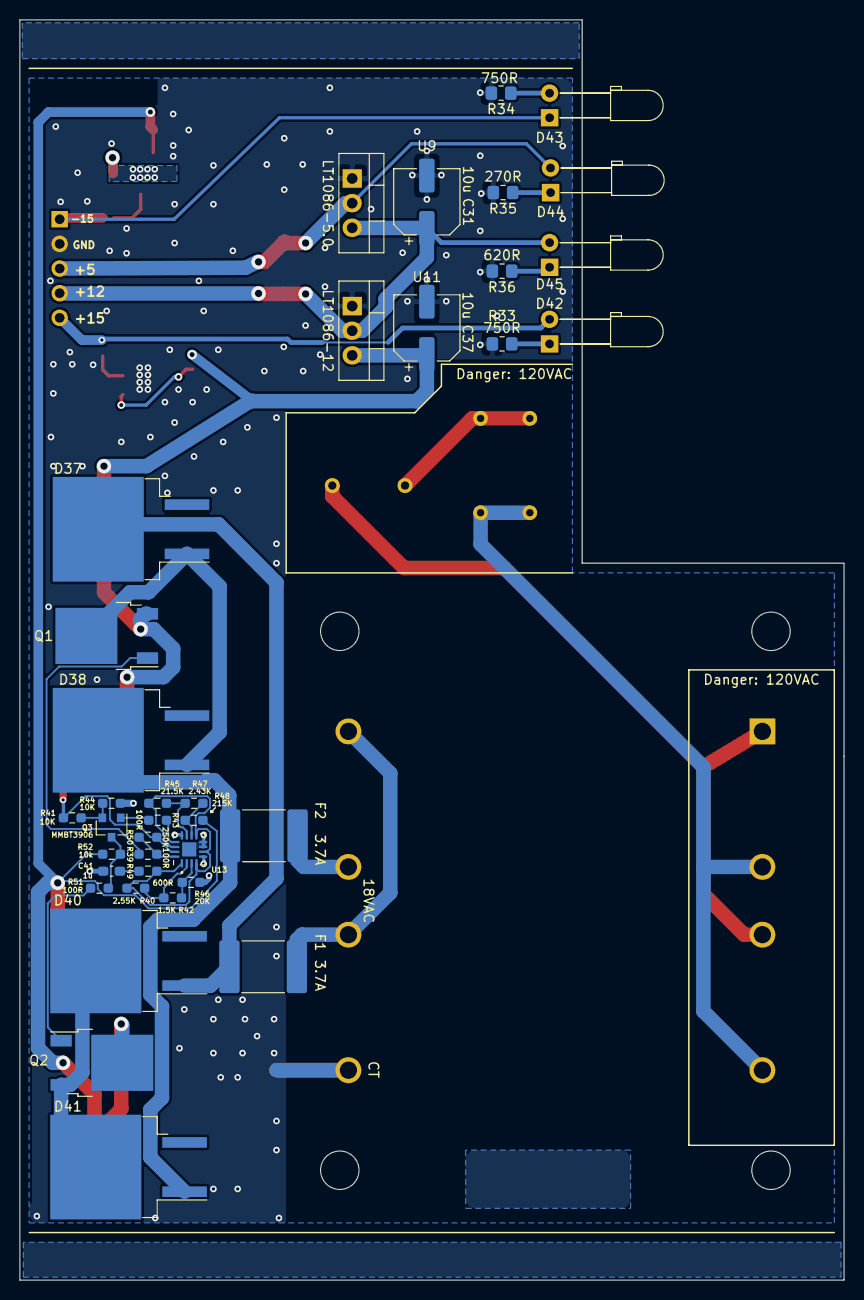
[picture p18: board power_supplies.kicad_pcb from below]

Board: 2 copper layers, 84.9 x 129.9 mm, 60 parts (37 on the bottom side), 35 nets.

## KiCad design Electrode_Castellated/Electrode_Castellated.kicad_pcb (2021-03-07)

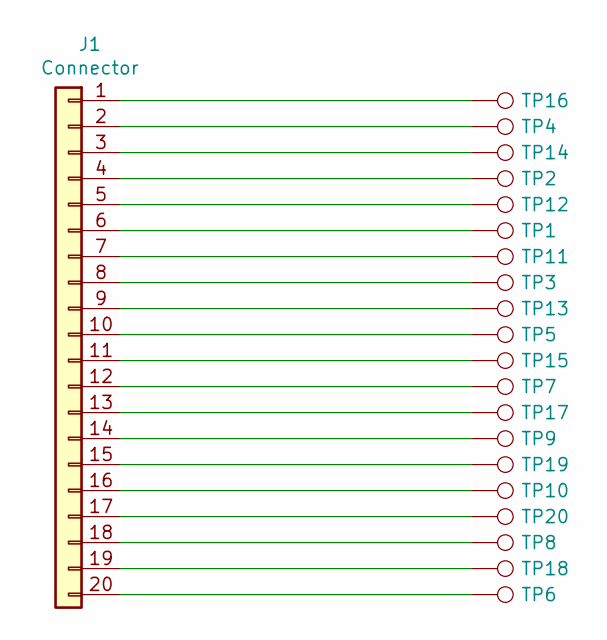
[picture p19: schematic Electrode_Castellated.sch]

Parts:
J1: Connector; Millmax Pad Contacts
TP1: 6; TestPoint_THTPad_D2.0mm_Drill1.0mm
TP2: 4; TestPoint_THTPad_D2.0mm_Drill1.0mm
TP3: 8; TestPoint_THTPad_D2.0mm_Drill1.0mm
TP4: 2; TestPoint_THTPad_D2.0mm_Drill1.0mm
TP5: 10; TestPoint_THTPad_D2.0mm_Drill1.0mm
TP6: 30; TestPoint_THTPad_D2.0mm_Drill1.0mm
TP7: 12; TestPoint_THTPad_D2.0mm_Drill1.0mm
TP8: 18; TestPoint_THTPad_D2.0mm_Drill1.0mm
TP9: 14; TestPoint_THTPad_D2.0mm_Drill1.0mm
TP10: 16; TestPoint_THTPad_D2.0mm_Drill1.0mm
TP11: 7; TestPoint_THTPad_D2.0mm_Drill1.0mm
TP12: 5; TestPoint_THTPad_D2.0mm_Drill1.0mm
TP13: 9; TestPoint_THTPad_D2.0mm_Drill1.0mm
TP14: 3; TestPoint_THTPad_D2.0mm_Drill1.0mm
TP15: 11; TestPoint_THTPad_D2.0mm_Drill1.0mm
TP16: 1; TestPoint_THTPad_D2.0mm_Drill1.0mm
TP17: 13; TestPoint_THTPad_D2.0mm_Drill1.0mm
TP18: 19; TestPoint_THTPad_D2.0mm_Drill1.0mm
TP19: 15; TestPoint_THTPad_D2.0mm_Drill1.0mm
TP20: 17; TestPoint_THTPad_D2.0mm_Drill1.0mm

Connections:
unnamed: J1.1, TP16.1
unnamed: J1.2, TP4.1
unnamed: J1.3, TP14.1
unnamed: J1.4, TP2.1
unnamed: J1.5, TP12.1
unnamed: J1.6, TP1.1
unnamed: J1.7, TP11.1
unnamed: J1.8, TP3.1
unnamed: J1.9, TP13.1
unnamed: J1.10, TP5.1
unnamed: J1.11, TP15.1
unnamed: J1.12, TP7.1
unnamed: J1.13, TP17.1
unnamed: J1.14, TP9.1
unnamed: J1.15, TP19.1
unnamed: J1.16, TP10.1
unnamed: J1.17, TP20.1
unnamed: J1.18, TP8.1
unnamed: J1.19, TP18.1
unnamed: J1.20, TP6.1


Board: 4 copper layers, 75.0 x 27.0 mm, 21 parts (0 on the bottom side), 20 nets.

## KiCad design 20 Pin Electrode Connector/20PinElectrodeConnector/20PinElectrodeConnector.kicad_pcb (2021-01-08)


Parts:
J1: Conn_02x10_Odd_Even; Millimax_817-22-020-30-001101
TP1, TP2, TP3, TP4, TP5, TP6, TP7, TP8, TP9, TP10, TP11, TP12, TP13, TP14, TP15, TP16, TP17, TP18, TP19, TP20: TestPoint; SolderWire-0.25sqmm_1x01_D0.65mm_OD2mm

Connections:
unnamed: J1.1, TP1.1
unnamed: J1.2, TP2.1
unnamed: J1.3, TP3.1
unnamed: J1.4, TP4.1
unnamed: J1.5, TP5.1
unnamed: J1.6, TP6.1
unnamed: J1.7, TP7.1
unnamed: J1.8, TP8.1
unnamed: J1.9, TP9.1
unnamed: J1.10, TP10.1
unnamed: J1.11, TP11.1
unnamed: J1.12, TP12.1
unnamed: J1.13, TP13.1
unnamed: J1.14, TP14.1
unnamed: J1.15, TP15.1
unnamed: J1.16, TP16.1
unnamed: J1.17, TP17.1
unnamed: J1.18, TP18.1
unnamed: J1.19, TP19.1
unnamed: J1.20, TP20.1


Board: 2 copper layers, 50.8 x 26.7 mm, 21 parts (0 on the bottom side), 20 nets.

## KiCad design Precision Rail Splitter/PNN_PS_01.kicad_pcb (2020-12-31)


Board: 2 copper layers, 89.1 x 45.4 mm, 31 parts (1 on the bottom side), 14 nets.

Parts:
C1, C2: 10uF; C_Elec_6.3x5.8
C3, C7: 100nF; C_0805_2012Metric_Pad1.18x1.45mm_HandSolder
C4: 10nF; C_0805_2012Metric_Pad1.15x1.40mm_HandSolder
C5, C6: 220uF; C_Elec_8x10.2
F1: 5A Fuse; Fuse_0805_2012Metric
H1, H2, H3: MountingHole; MountingHole_5.3mm_M5_ISO14580
HS1, HS2: Heatsink; courtyardfix_Heatsink_Fischer_SK104-STC-STIC_35x13mm_2xDril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
J1: Input; EM274202H
J2: Output; EM274203H
Q1: 2N2222; SOT-723
Q2: TIP122; TO-220-3_Vertical
Q3: TIP127; TO-220-3_Vertical
R1, R2: 10K; R_0805_2012Metric_Pad1.15x1.40mm_HandSolder
R3: 14R; R_0805_2012Metric_Pad1.15x1.40mm_HandSolder
R4: 5.62K; R_0805_2012Metric_Pad1.15x1.40mm_HandSolder
R5: 1.1K; R_0805_2012Metric_Pad1.15x1.40mm_HandSolder
R6, R7: 1R; TO-220-2_Vertical
R8, R9: 49.9K; R_1206_3216Metric_Pad1.30x1.75mm_HandSolder
RV1: 1K; Potentiometer_Bourns_3214W_Vertical
RV2: 1 K; Potentiometer_Bourns_3296W_Vertical
U1: NE5532; SOIC-8_3.9x4.9mm_P1.27mm
U2: LM334; TO-92_Inline_Wide

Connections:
+9V: C1.1, C3.1, C5.1, F1.2, J2.1, Q2.2, R1.1, R3.1, R8.1, U1.8, U2.1
-9V: C2.2, C3.2, C6.2, C7.1, J1.1, J2.3, Q3.3, R2.2, R4.2, R9.2, U1.4
GND: C5.2, C6.1, J2.2, R6.2, R7.1, U1.2, U1.5
unnamed: C1.2, C2.1, R1.2, R2.1, RV2.2, U1.3
unnamed: C4.1, Q1.3, Q2.1, R5.1, U2.3
unnamed: C4.2, Q1.1, Q3.1, R4.1, RV1.2, RV1.3, U1.1
unnamed: C7.2, F1.1, J1.2
unnamed: Q1.2, R5.2, RV1.1
unnamed: Q2.3, R6.1
unnamed: Q3.2, R7.2
unnamed: R3.2, U2.2
unnamed: R8.2, RV2.1
unnamed: R9.1, RV2.3
unnamed: U1.6, U1.7

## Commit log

2020-12-31 Moving old project into new repo
    [PNN_PS_01.kicad_pcb, PNN_PS_01.sch]
2020-12-31 Fix git submodule issue
    [PNN_PS_01.kicad_pcb, PNN_PS_01.sch]
2020-12-31 Add Zenner to keep xfrmr output below LT3045 abs max on low load, remove cap multiplier
    [power_supplies.sch]
2021-01-01 Change txfrmrs to VPP series, change 10V txfrmr to 12V to improve regulation
    [power_supplies.sch]
2021-01-02 Remove mysterious output resistors from 3094 app note.
    [power_supplies.sch]
2021-01-02 Add SCR pre-reg for +15V rail
    [power_supplies.sch]
2021-01-02 Add SCR pre-reg for -15V rail
    [power_supplies.sch]
2021-01-03 Add SCR pre-reg for 5V rail
    [power_supplies.sch]
2021-01-03 parallel fet on 5v prereg
    [power_supplies.sch]
2021-01-03 Add simulations and relay state spreadsheet
    [io_ports_panels.sch, multiplexer.sch, power_supplies.sch, relay_state_features.ods]
2021-01-04 Elminate extra scope cal relay, re-organize relays, re-annotate, ERC
    [DUT_Selector.sch, io_ports_panels.sch, meas_sel.sch, multiplexer.sch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]
2021-01-06 Switch to pogo pin style connector pads
    [Electrode_Castellated.kicad_pcb, Electrode_Castellated.sch]
2021-01-06 Move power flags
    [power_supplies.sch]
2021-01-06 Electrode connector initial commit.
    [20PinElectrodeConnector.kicad_pcb, 20PinElectrodeConnector.sch]
2021-01-08 Conform to microscope stage bracket.
    [20PinElectrodeConnector.kicad_pcb, 20PinElectrodeConnector.sch]
2021-01-08 Update to pogo pin pads.
2021-01-08 Add footprints for low precision/low power parts.
    [ammeter.sch, io_ports_panels.sch, power_supplies.sch, relay_driver.sch]
2021-01-10 More footprints added.
    [ammeter.sch, io_ports_panels.sch, power_supplies.sch, relay_driver.sch]
2021-01-12 NTC calulations/specs done.
    [power_supplies.sch]
2021-01-12 Footprint updates
    [ammeter.sch, impedance_analyzer.sch, io_ports_panels.sch, multiplexer.sch]
2021-01-27 +15V LTSpice sim with pre-reg
2021-01-27 Remove edison plug from schematic, now wire holes.
    [power_supplies.sch]
2021-01-28 Comparator supply -> single-ended
    [power_supplies.sch]
2021-02-11 Switch to 28V txfrmr, nix preregs, nix 5V for AD2, switch to 12V relay power.
    [DUT_Selector.sch, ammeter.sch, impedance_analyzer.sch, io_ports_panels.sch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]
2021-02-20 Reannotate, power supply schematic improvements, begin power supply layout.
    [DUT_Selector.sch, IO_Control.sch, Sources_Flux.sch, ammeter.sch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]
2021-02-27 Change power entry module to fit enclosure.
    [power_supplies.sch]
2021-02-27 Initial component layout.
    [power_supplies.kicad_pcb]
2021-03-01 Update LT3045 symbol w/ missing pins.
    [power_supplies.sch]
2021-03-01 Begin routing traces.
    [power_supplies.kicad_pcb]
2021-03-02 HV and rectification sections routed.
    [power_supplies.kicad_pcb]
2021-03-04 Back to kelvin connection on +-15 reg out cap
    [power_supplies.sch]
2021-03-04 Finish routing low voltage side, silkscreen
    [power_supplies.kicad_pcb]
2021-03-05 Add crowbar protection for regulator inputs.
    [power_supplies.kicad_pcb, power_supplies.sch]
2021-03-05 Fix silks overlapping with vias.
    [power_supplies.kicad_pcb]
2021-03-05 Daisy-chain 12V->5V regs.
    [power_supplies.kicad_pcb, power_supplies.sch]
2021-03-05 Auto-cleanup tracks and vias
    [power_supplies.kicad_pcb]
2021-03-07 Improved crowbar performance. Posted for reddit design review.
    [power_supplies.kicad_pcb, power_supplies.sch]
2021-03-07 Fix silkscreen labels, add dimensions & SN
    [Electrode_Castellated.kicad_pcb, Electrode_Castellated.sch]
2021-03-11 Replace crowbar with LTC2966.
    [power_supplies.sch]
2021-03-11 Increase ptc fuse size to 3.7 A, update FPs.
    [power_supplies.sch]
2021-03-11 Switch to QFN package for LTC2966.
    [power_supplies.sch]
2021-03-16 Recalculate resistor values and select pass FETs.
    [power_supplies.sch]
2021-03-16 Route LTC2966 addition and remove pin 2 connections.
    [power_supplies.kicad_pcb]
2021-03-16 Silkscreen fixes
    [power_supplies.kicad_pcb]
2021-03-17 Switch to opa1622 for greater stability.
    [ammeter.sch]
2021-03-17 Switch to TVS flyback diodes.
    [relay_driver.sch]
2021-03-17 Design review 2
    [power_supplies.kicad_pcb, power_supplies.sch]
2021-03-20 Fix symbols for OPA189 and 192.
    [ammeter.sch]
2021-03-20 Schematic layout of ps section complete.
    [SMU Shunt Amp.kicad_pcb, SMU Shunt Amp.sch]
2021-03-21 Schematic finished.
    [SMU Shunt Amp.sch]
2021-03-21 Reduce voltage rails to +/-14V
    [SMU Shunt Amp.sch]
2021-03-21 Begin PCB layout
    [SMU Shunt Amp.kicad_pcb]
2021-03-22 Fix null pin and add thermal pad pin to THS 4021
2021-03-22 90% finished routing PCB.
    [SMU Shunt Amp.sch]
2021-03-24 PCB sent to manufacturer.
    [SMU Shunt Amp.kicad_pcb]
2021-03-24 BOM complete.
    [BOM.csv]
2021-03-24 As sent to PCB manufacture.
2021-03-24 Add part numbers to schematic.
    [SMU Shunt Amp.sch]
2021-03-31 Redesign with analog switches.
    [DUT_Selector.sch, io_ports_panels.sch, shunts.sch]
2021-04-01 Add latching relay driver for integrator reset.
    [SMUTestFixture.sch]
2021-04-02 Add analog switch power connections.
    [DUT_Selector.sch, SMUTestFixture.sch, shunts.sch]
2021-04-13 Rev B changes. THS4021 footprint fix, nulling circuit corrections, gnd tp cur limit.
    [SMU Shunt Amp.kicad_pcb, SMU Shunt Amp.sch]
2021-04-16 Keepout and text tweaks
    [SMU Shunt Amp.kicad_pcb]
2021-05-05 New composite staged CFB design.
    [SMU Shunt Amp.kicad_pcb, SMU Shunt Amp.sch]
2021-05-06 PCB layout initial.
    [SMU Shunt Amp.kicad_pcb, SMU Shunt Amp.sch]
2021-05-08 More vias
    [SMU Shunt Amp.kicad_pcb]
2021-05-10 Add ferrites
    [SMU Shunt Amp.sch]
2021-05-10 Thicken output paths, add ferrites.
    [SMU Shunt Amp.kicad_pcb]
2021-05-12 New layout for better signal integrity
    [SMU Shunt Amp.kicad_pcb]
2021-05-14 Most routing done.
    [SMU Shunt Amp.kicad_pcb]
2021-05-20 Before *big* OPA189 move.
    [SMU Shunt Amp.kicad_pcb]
2021-05-21 Rollback 189 move, tighten FB path, improve power routing.
    [SMU Shunt Amp.kicad_pcb]
2021-06-02 Finish layout for design review.
    [SMU Shunt Amp.kicad_pcb]
2021-06-03 Remove fb caps after more sims. Increase fb resistors in hs loop.
    [SMU Shunt Amp.kicad_pcb]
2021-06-04 Better grounding for OPA189 +V bypass
    [SMU Shunt Amp.kicad_pcb]
2021-07-02 Move OPA189 output to THS3092 + for stability
    [SMU Shunt Amp.sch]
2021-07-08 Rev C changes, opa189 now on ths3092 +
    [SMU Shunt Amp.kicad_pcb]
2021-07-12 Add new shunt amp design to SMU schematic.
    [SMUTestFixture.sch]
2021-08-09 Fix via DRC error. Reroute protection zener.
    [SMU Shunt Amp.kicad_pcb]
2022-09-28 Convert to KiCad 6
    [power_supplies.kicad_pcb, power_supplies.sch]
2022-09-29 KiCad 6 Files with SPI additions
    [DUT_Selector.kicad_sch, DUT_Selector.sch, SMUTestFixture.kicad_pcb, SMUTestFixture.kicad_sch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]
2022-09-29 Move bypass caps to devices
    [SMU Shunt Amp.kicad_pcb, SMUTestFixture.kicad_sch, io_and_ports.kicad_sch]
2022-09-29 Use relay for wavegen output termination.
    [SMUTestFixture.kicad_sch, io_and_ports.kicad_sch]
2022-09-29 Add buffered vdut output
    [SMUTestFixture.kicad_sch]
2022-09-29 Add measurement connections to scope inputs
    [SMUTestFixture.kicad_sch, io_and_ports.kicad_sch]
2022-09-30 Fix grid nightmare. Begin adding bypass caps for a.switches
    [DUT_Selector.kicad_sch, SMUTestFixture.kicad_sch, io_and_ports.kicad_sch, power_supplies.kicad_sch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]
2022-09-30 Finish adding bypass for all a.switches
    [DUT_Selector.kicad_sch, SMUTestFixture.kicad_sch, io_and_ports.kicad_sch]
2022-09-30 Split ADGS1408 units, add switch contorl page
    [DUT_Selector.kicad_sch, SMUTestFixture.kicad_sch, io_and_ports.kicad_sch, power_supplies.kicad_sch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]
2022-10-01 Symbol fixes, ERC pass
    [DUT_Selector.kicad_sch, SMUTestFixture.kicad_sch, io_and_ports.kicad_sch, power_supplies.kicad_sch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]
2022-12-09 Fix incorrect kill pin
2022-12-09 Use TypedDict for pin assignments
2022-12-17 Allow user play when no device connected
